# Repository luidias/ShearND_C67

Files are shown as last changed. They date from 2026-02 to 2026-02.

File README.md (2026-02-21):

# Noninjurious C6C7 Shear Data
This repository contains processed data used in the analysis of the biomechanical response of thirty-nine human Functional Spinal Units (FSUs) at the C6/C7 level when subjected to  pure shear loading. This data is provided here in full to facilitate FE model validation efforts. Detailed models of test fixturing is also included.

## Fixturing
This directory contains fixturing models and necessary information for their use.

- 'Assembly Diagrams.pdf' contains a labeled Bill of Materials and a schematic of how the components are assembled
- 'Fixturing Guide.pdf' contains information on fixture alignment as well as shear load and balancing mass application locations, and a more detailed Bill of Materials.

### Solidworks
This subdirectory contains models of all components (.SLDPRT) and the full assembly (.SLDASM) of the fixturing, generated in Solidworks 2025.

### STEP

This subdirectory contains models of all components as .STEP files, for wider compatibility with other CAD software. 
- The 'Individual Components' folder contains all component files separately.
- The 'Joined Components' folder contains aggregated .STEP files for the main fixturing and the mobile carriage. These must be positioned relative to each other according to the Disc Offset parameter. See the "Fixturing Guide" document for more details.

## Load-Displacement data

This directory contains sub-directories for each specimen (H1, H2, etc.), which in turn contain .csv files for individual tests on the given specimen. There are six files per specimen, one for each test condition (Anterior/posterior directions and 1, 10, and 100 mm/s). Test condition is reflected in the file name.

These files contain the 3D displacements, rotations, and loads that were experienced by the FSU under the respective test condition. The X, Y, and Z axes were aligned with the anatomical axes:
- X axis: Anteroposterior axis, with anterior as the positive direction. Shear loads were applied along this axis.
- Y axis: Craniocaudal (superior-inferior) axis. Cranial (superior) is positive.
- Z axis: Lateral axis. Right is positive.
  
Rotations around each axis follow the right hand rule: with the axis pointing out of the page, positive rotations are counter-clockwise.

The .csv files are laid out such that:
- Columns 1-3 are the X, Y, Z displacements of the superior vertebra relative to the inferior, measured im mm.
- Columns 4-6 are the X, Y, Z rotations of the same, measured in degrees.
- Columns 7-9 are the X, Y, Z loads generated during the test.
- Columns 10-12 are the X, Y, Z moments generated during the test, in Newton-Meters.

## Specimen Info.csv

This file contains demographic and anthropometric data for each specimen.
- **ID**: Identifier code for the specimen. Matches corresponding sub-directory in Load-displacement data directory.
- **Level**: FSU level. For this dataset, all specimens were at the C6/C7 level.
- **CT_Scanned**: Boolean representing whether CT scans were taken of the specimen.
- **ND_Test_Date**: Date when testing occured, in MM/DD/YYYY format.
- **Disc_Offset_mm**: The offset between the superior side of the fixturing and the load application point, adjusted for each specimen such that the loading line of action goes through the mid-disc plane, ensuring pure shear without any bending moment.
- **Specimen_Mass_kg**: Mass of the specimen, in kg, including PMMA potting, reinforcements, and specimen mounting plates
- **Balancing_Mass_kg**: Counterbalance mass used for the test, in kg, made up of half of the total specimen mass and the mass of the superior fixturing hardware.
- **Age**: Age of donor, in years.
- **Sex**: Biological sex of donor.
- **Race**: Race of donor.
- **Weight_kg**: Weight of donor at time of death, in kg.
- **Height_cm**: Height of donor at time of death, in cm.
- **Cause_of_death**: Donor cause of death.
- **sup_endplate_ap_width_from_lat_view_mm**: AP width of superior endplate proximal to the C6/C7 intervertebral disc, in mm. Measurements were taken from lateral X-ray images.
- **inf_endplate_ap_width_from_lat_view_mm**: Same as above, for the inferior endplate proximal to the disc.
- **avg_ap_width_from_lat_view_mm**: Average AP width of both proximal endplates.
- **avg_fsu_vertebral_body_volume_mm3**: averaged volume of the cancellous bone of both vertebral bodies, in mm<sup>3</sup>.
- **avg_vert_body_treb_bv_fraction**: Average bone volume fraction (BV/TV) of the cancellous bone in both vertebral bodies, as a ratio of bone volume to total volume.
- **Disc_Degen_Score**: Disc degeneration score, per the method established by Walraevens et al. [1], graded using CT scans. This is the sum of scores given to the disc for height loss, osteophytes, and endplate sclerosis. Possible scores are 0-9, where higher scores represent more degenerated discs.
- **Disc_Degen_Grade**: Disc degeneration grades correponding to the score. Possible values are None, Mild, Moderate, or Severe.
- **DD_Height_Loss**: Disc Height loss score. Possible scores of 0-4.
- **DD_Ant_OP**: Score for presence of anterior osteophytes, based on osteophyte size. Possible scores of 0-3.
- **DD_Endplate_Sclerosis**: Score for presence of proximal endplate sclerosis, based on severity. Possible scores of 0-2.
- **FJ_Degen_Score**: Facet Joint degeneration score, per Walraevens et al. [1], graded using CT scans. This is the sum of scores given for hypertrophy, osteophytes, articular irregularities, and joint space narrowing. Possible scores are 0-5, where higher scores represent more degenerated facet joints.
- **FJ_Degen_Grade**: Facet Joint degeneration grades correponding to the score. Possible values are None, Mild, Moderate, or Severe.
- **FJD_Hypertrophy**: Score for presence of hypertrophy. Possible scores are 0-2.
- **FJD_Osteophytes**: Score for presence of osteophytes. Possible scores are 0 or 1.
- **FJD_Surface_Irregularity**: Score for irregularity of articular surfaces. Possible scores are 0 or 1.
- **FJD_Joint_Narrowing**: Score for joint space narrowing. Possible scores are 0 or 1.

## Test Info.csv

This file contains information on specific tests carried out on the specimens. Each row entry represents one test. Specimen-specific data is repeated from Specimen Info.csv. Test-specific data is described below:
- **direction**: direction in which shear loads were applied (anterior or posterior).
- **disp_rate_mm_s**: displacement rate at which the test was carried out, in mm/s.
- **stiffness_1**: The Phase I Stiffness, in N/mm, calculated from the slope of the load-displacement data using a breakpoint analysis.
- **stiffness_2**: The Phase II Stiffness, in N/mm, calculated from the slope of the load-displacement data using a breakpoint analysis.
- **intercept_1**: Y-intercept of the linear regression from which Phase I stiffness was taken.
- **intercept_2**: Y-intercept of the linear regression from which Phase II stiffness was taken.
- **breakpoint_mm**: Location of breakpoint between the Phase I and Phase II response, on the displacement axis.
- **Calculated R2_1**: Goodness of fit (R<sup>2</sup>) for the Phase I regression line.
- **Calculated R2_2**: Goodness of fit (R<sup>2</sup>) for the Phase II regression line.
- **Calculated R2_3**: Goodness of fit (R<sup>2</sup>) for both regression lines in the breakpoint analysis.
- **peakLoad_N**: Maximum shear load during the test, in N.
- **peakDisp_mm**: maximum displacement during the test, in mm.

## References
[1] Walraevens J, Liu B, Meersschaert J, Demaerel P, Delye H, Depreitere B, et al. Qualitative and quantitative assessment of degeneration of cervical intervertebral discs and facet joints. Eur Spine J Off Publ Eur Spine Soc Eur Spinal Deform Soc Eur Sect Cerv Spine Res Soc. 2009 Mar;18(3):358–69

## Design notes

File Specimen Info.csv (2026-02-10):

ID | Level | CT_Scanned | ND_Test_Date | Disc_Offset_mm | Specimen_Mass_kg | Balancing_Mass_kg | Age | Sex | Race | Weight_kg | Height_cm | Cause_of_Death | sup_enplate_ap_width_from_lat_view_mm | inf_enplate_ap_width_from_lat_view_mm | avg_ap_width_from_lat_view_mm | avg_fsu_vertebral_body_volume_mm3 | avg_vert_body_treb_bv_fraction | Disc_Degen_Score | Disc_Degen_Grade | DD_Height_Loss | DD_Ant_OP | DD_Endplate_Sclerosis | FJ_Degen_Score | FJ_Degen_Grade | FJD_Hypertrophy | FJD_Osteophytes | FJD_Surface_Irregularity | FJD_Joint_Narrowing
H1 | C6C7 | TRUE | 7/8/2022 | 31.1 | 2.069 | 2.6535 | 67 | M | Caucasian | 120 | 180 | Myocardial Infarction | 15.4 | 14 | 14.7 | 1961.84 | 0.2045 | 1 | mild | 0 | 0 | 1 | 1 | mild | 0 | 0 | 0 | 1
H2 | C6C7 | TRUE | 6/29/2022 | 34.89 | 2.063 | 2.6505 | 73 | F |  |  |  |  | 16.5 | 15.7 | 16.1 | 1940.41 | 0.017 | 1 | mild | 0 | 1 | 0 | 1 | mild | 0 | 1 | 0 | 0
H3 | C6C7 | TRUE | 7/27/2022 | 28 | 2.04 | 2.639 | 69 | M |  |  |  |  | 17.3 | 16.8 | 17.05 | 2816.95 | 0.092 | 0 | none | 0 | 0 | 0 | 1 | mild | 0 | 1 | 0 | 0
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

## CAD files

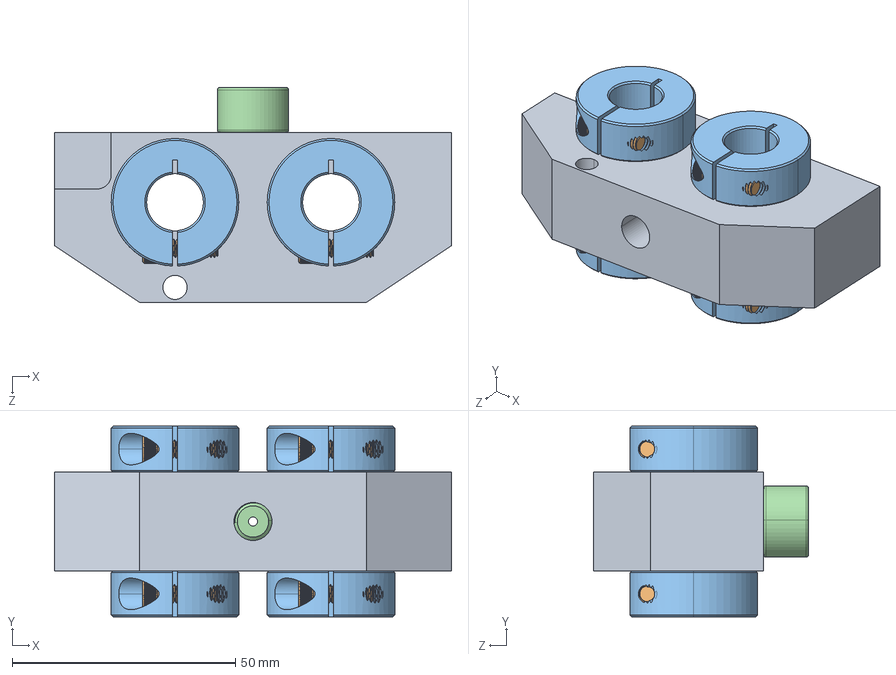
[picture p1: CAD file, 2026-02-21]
Fixturing/STEP/Joined Components/ND_Shear_Assembly_SinglePart_CarriageOnly.STEP
88.9 x 42.7 x 48.1 mm

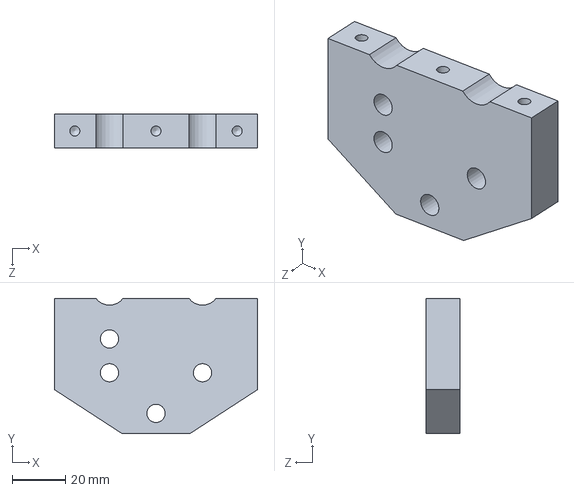
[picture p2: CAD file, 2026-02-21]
Fixturing/Solidworks/Outer gantry bracket, lower.SLDPRT
76.2 x 50.8 x 12.7 mm

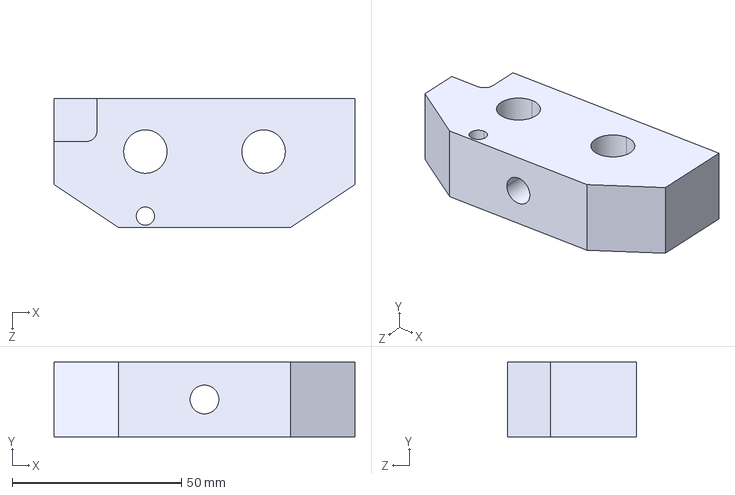
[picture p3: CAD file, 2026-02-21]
Fixturing/STEP/Individual components/Gantry Block.STEP
88.9 x 22.1 x 38.1 mm

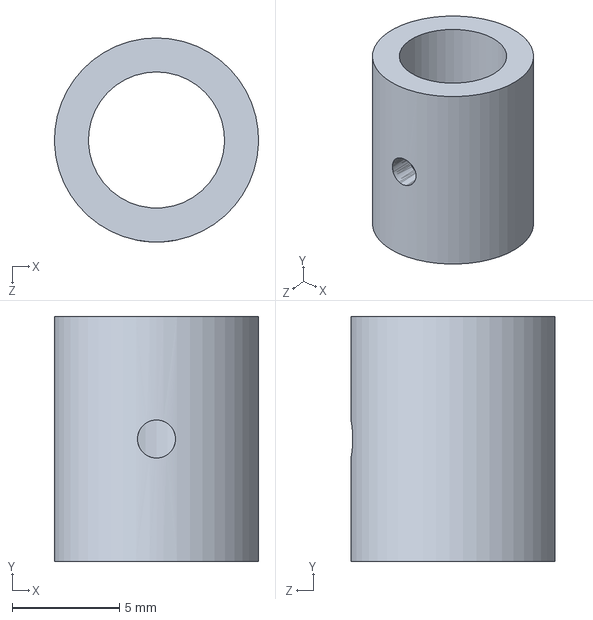
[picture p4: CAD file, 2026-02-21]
Fixturing/Solidworks/Spacer, small.SLDPRT
9.52 x 11.4 x 9.53 mm

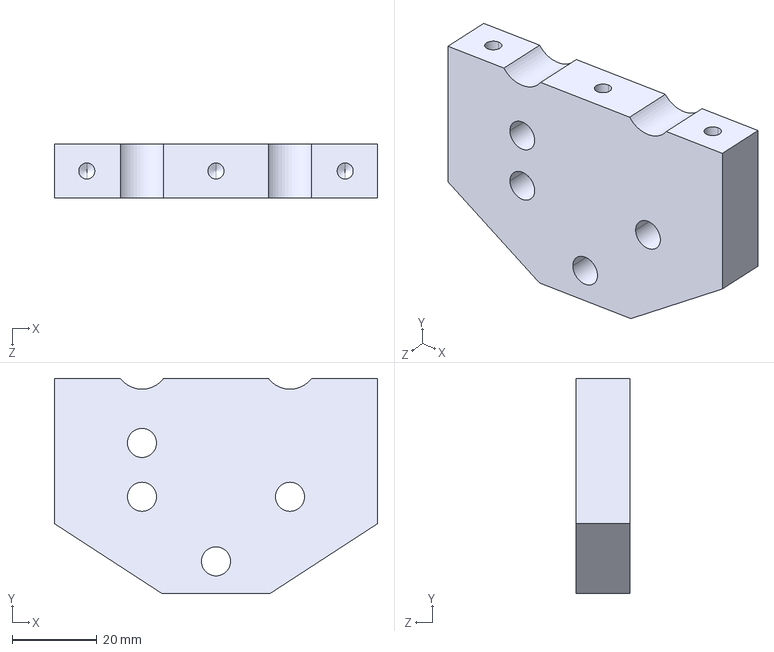
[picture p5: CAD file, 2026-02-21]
Fixturing/STEP/Individual components/Outer gantry bracket, lower.STEP
76.2 x 50.8 x 12.7 mm

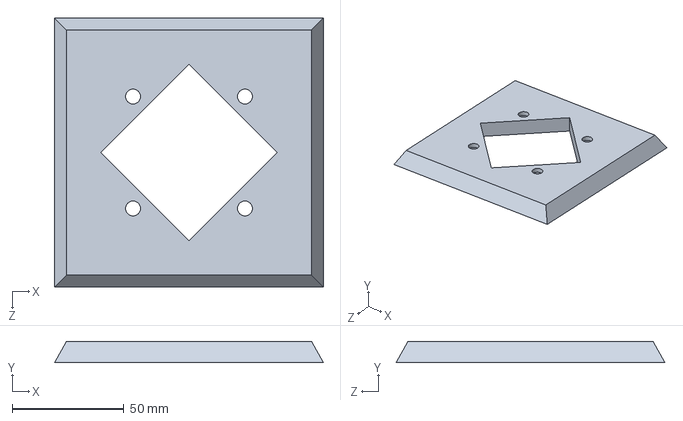
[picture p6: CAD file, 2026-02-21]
Fixturing/Solidworks/Specimen mounting plate.SLDPRT
120.2 x 9.53 x 120.2 mm

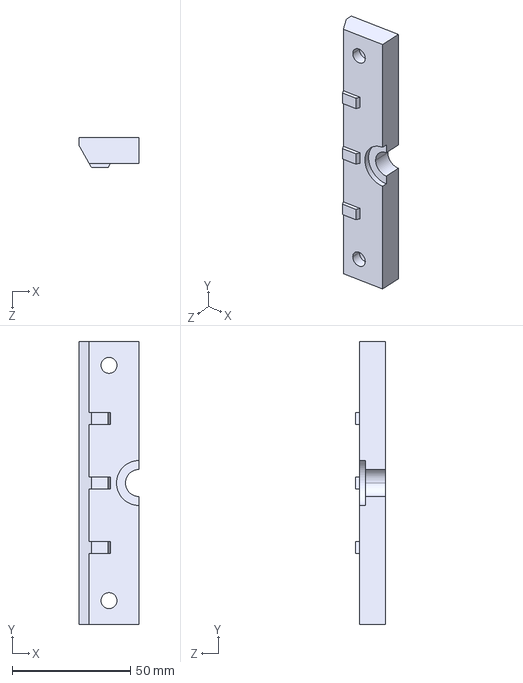
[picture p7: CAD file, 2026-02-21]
Fixturing/STEP/Individual components/Upper retainer.STEP
25.4 x 119.9 x 12.7 mm

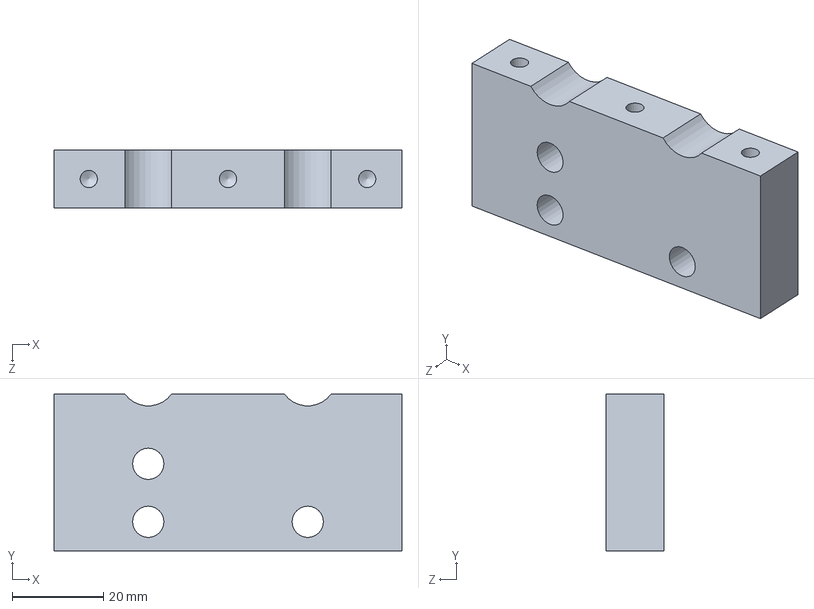
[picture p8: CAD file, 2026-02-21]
Fixturing/Solidworks/Inner gantry bracket, lower.SLDPRT
76.2 x 34.3 x 12.7 mm

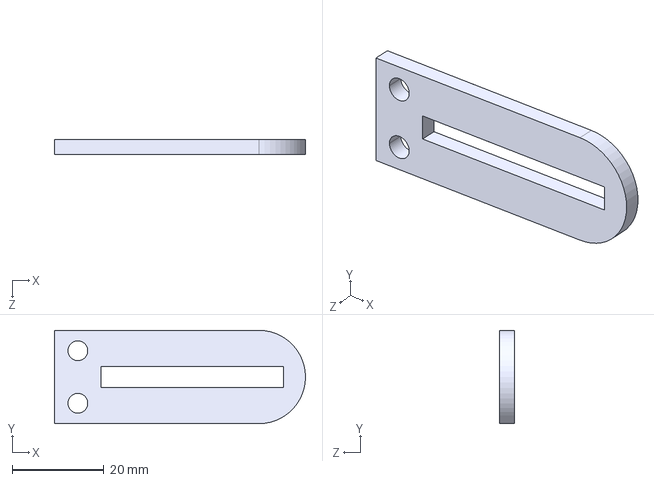
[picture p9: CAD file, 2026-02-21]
Fixturing/STEP/Individual components/Balancing bracket.STEP
54.6 x 20.3 x 3.17 mm

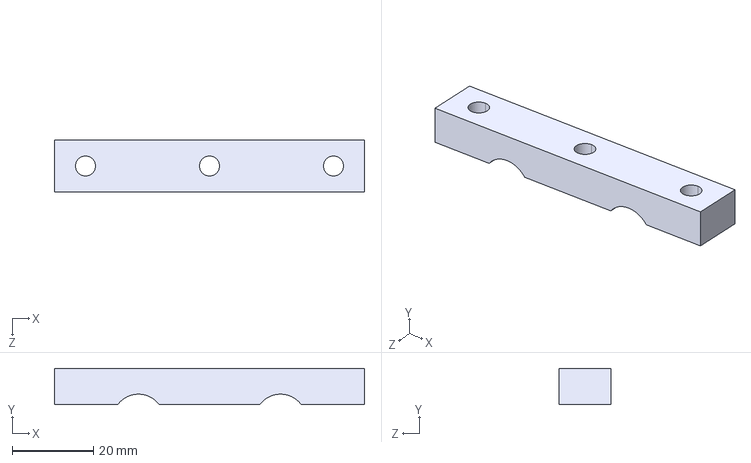
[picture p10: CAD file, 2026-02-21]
Fixturing/STEP/Individual components/Outer gantry bracket, upper.STEP
76.2 x 8.89 x 12.7 mm

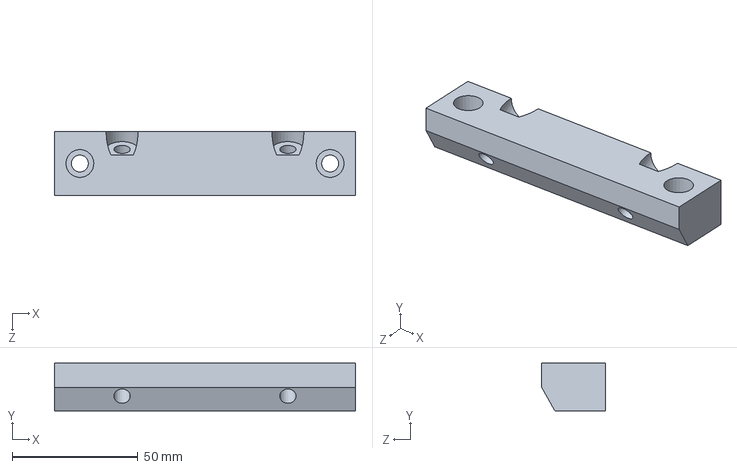
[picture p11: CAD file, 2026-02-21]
Fixturing/Solidworks/Lower retainer.SLDPRT
119.9 x 19.1 x 25.4 mm

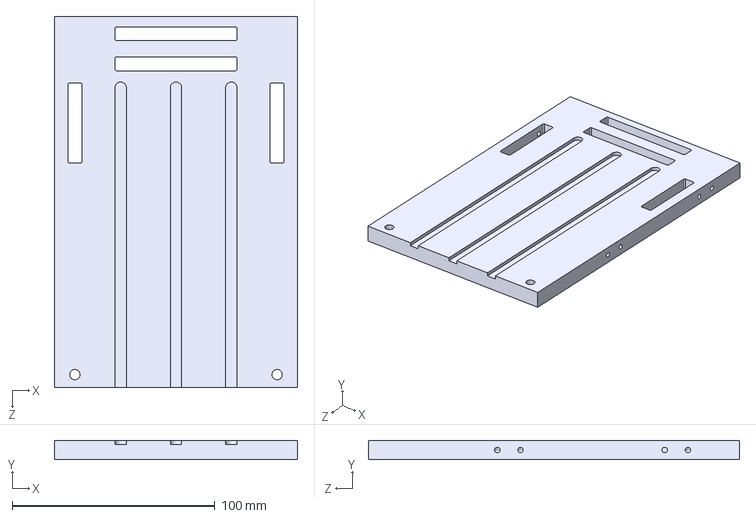
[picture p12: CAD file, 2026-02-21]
Fixturing/STEP/Individual components/Backing Plate.STEP
119.9 x 9.53 x 182.9 mm

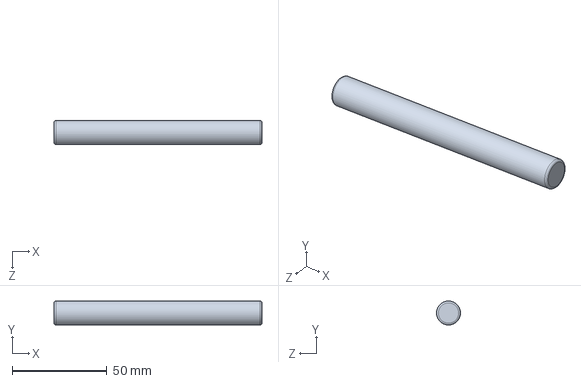
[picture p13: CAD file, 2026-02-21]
Fixturing/Solidworks/Gantry Rod.SLDPRT
110.0 x 12.7 x 12.7 mm

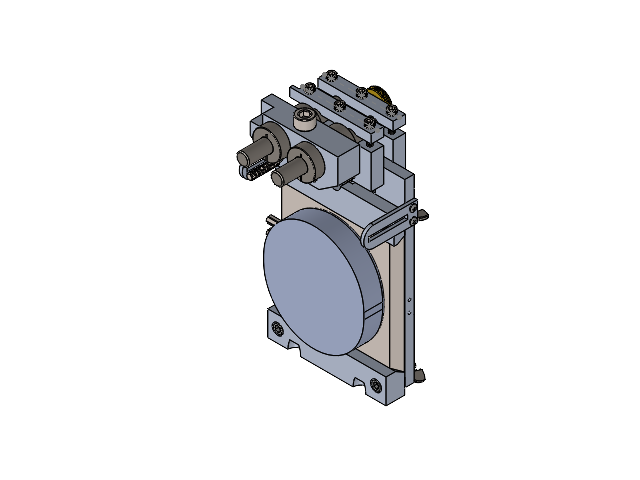
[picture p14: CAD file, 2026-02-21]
Fixturing/Solidworks/ND_Shear_Assembly.SLDASM
Backing Plate
5125K52_Brass Knob
Gantry Block
Gantry Rod x 2
Inner gantry bracket, lower
Inner gantry bracket, upper
Outer gantry bracket, lower
Outer gantry bracket, upper
Spacer, large
Spacer, small
92185A214_Super-Corrosion-Resistant 316 Stainless Steel Socket Head Screw x 6
90499A029_High-Strength Steel Hex Nut x 3
6435K34_Clamping Shaft Collar x 4
90126A206_Zinc-Plated Steel SAE Washer x 4
92580A332_Grade B7 Medium-Strength Steel Threaded Rod
92185A544_Super-Corrosion-Resistant 316 Stainless Steel Socket Head Screw
92185A548_Super-Corrosion-Resistant 316 Stainless Steel Socket Head Screw x 2
Lower retainer
Upper retainer
Specimen mounting plate
90866A029_Zinc-Plated Steel Wing Nut x 4
92196A540_18-8 Stainless Steel Socket Head Screw x 2
92196A544_18-8 Stainless Steel Socket Head Screw x 2
92311A581_18-8 Stainless Steel Cup-Point Set Screw x 2
91075A445_Male-Female Threaded Hex Standoff x 2
Balancing bracket x 2
91772A146_Passivated 18-8 Stainless Steel Pan Head Phillips Screw x 4
92196A537_18-8 Stainless Steel Socket Head Screw x 4
Cranial Potting
91292A046_18-8 Stainless Steel Socket Head Screw
92311A077_18-8 Stainless Steel Cup-Point Set Screw x 3

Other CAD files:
Fixturing/STEP/Individual components/ND_Shear_Assembly.STEP
Fixturing/Solidworks/Balancing bracket.SLDPRT
Fixturing/Solidworks/Gantry Block.SLDPRT
Fixturing/Solidworks/Outer gantry bracket, upper.SLDPRT
Fixturing/STEP/Individual components/5125K52_Brass Knob_5125K52.STEP
Fixturing/STEP/Individual components/6435K34_Clamping Shaft Collar_6435K34.STEP
Fixturing/STEP/Individual components/90126A206_Zinc-Plated Steel SAE Washer_90126A206.STEP
Fixturing/STEP/Individual components/90499A029_High-Strength Steel Hex Nut_90499A029.STEP
Fixturing/STEP/Individual components/90866A029_Zinc-Plated Steel Wing Nut_90866A029.STEP
Fixturing/STEP/Individual components/91075A445_Male-Female Threaded Hex Standoff_91075A445.STEP
Fixturing/STEP/Individual components/91292A046_18-8 Stainless Steel Socket Head Screw_91292A046.STEP
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

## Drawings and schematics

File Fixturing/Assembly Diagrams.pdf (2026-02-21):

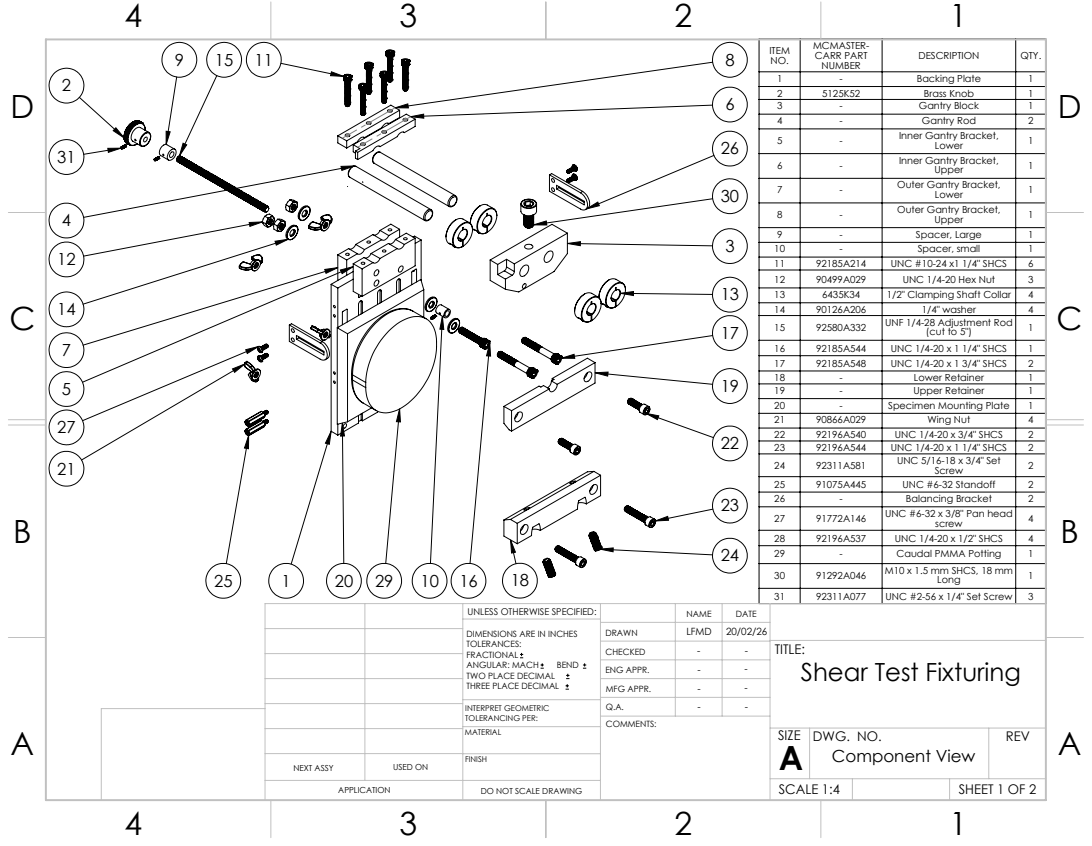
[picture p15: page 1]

ITEM NO. | MCMASTER-CARR PART NUMBER | DESCRIPTION | QTY.

1 | - Backing Plate | | 1
2 | 5125K52 | Brass Knob | 1
3 | - Gantry Block | | 1
4 | - Gantry Rod | | 2
5 | - Inner Gantry Bracket, | Lower | 1
6 | - Inner Gantry Bracket, | Upper | 1
7 | - Outer Gantry Bracket, | Lower | 1
8 | - Outer Gantry Bracket, | Upper | 1
9 | - Spacer, Large | | 1
10 | - Spacer, small | | 1
11 | 92185A214 | UNC #10-24 x1 1/4" SHCS | 6
12 | 90499A029 | UNC 1/4-20 Hex Nut | 3
13 | 6435K34 | 1/2" Clamping Shaft Collar | 4
14 | 90126A206 | 1/4" washer | 4
15 | 92580A332 | UNF 1/4-28 Adjustment Rod (cut to 5") | 1

16 | 92185A544 | UNC 1/4-20 x 1 1/4" SHCS | 1
17 | 92185A548 | UNC 1/4-20 x 1 3/4" SHCS | 2
18 | - Lower Retainer | | 1
19 | - Upper Retainer | | 1
20 | - Specimen Mounting Plate | | 1
21 | 90866A029 | Wing Nut | 4
22 | 92196A540 | UNC 1/4-20 x 3/4" SHCS | 2
23 | 92196A544 | UNC 1/4-20 x 1 1/4" SHCS | 2
24 | 92311A581 | UNC 5/16-18 x 3/4" Set Screw | 2
25 | 91075A445 | UNC #6-32 Standoff | 2
26 | - Balancing Bracket | | 2
27 | 91772A146 | UNC #6-32 x 3/8" Pan head screw | 4
28 | 92196A537 | UNC 1/4-20 x 1/2" SHCS | 4
29 | - Caudal PMMA Potting | | 1
30 | 91292A046 | M10 x 1.5 mm SHCS, 18 mm Long | 1

31 | 92311A077 | UNC #2-56 x 1/4" Set Screw | 3

UNLESS OTHERWISE SPECIFIED: | | NAME | DATE
DIMENSIONS ARE IN INCHES TOLERANCES: FRACTIONAL ANGULAR: MACH BEND TWO PLACE DECIMAL THREE PLACE DECIMAL | DRAWN | LFMD

CHECKED | | 20/02/26 --- | TITLE: Shear Test Fixturing
ENG APPR. | ---

MFG APPR.

INTERPRET GEOMETRIC TOLERANCING PER: | Q.A. | - | -
MATERIAL | | SIZE A | DWG. NO. Component View | REV

NEXT ASSY | USED ON | FINISH

APPLICATION | DO NOT SCALE DRAWING | | SCALE 1:4 | | SHEET 1 OF 2

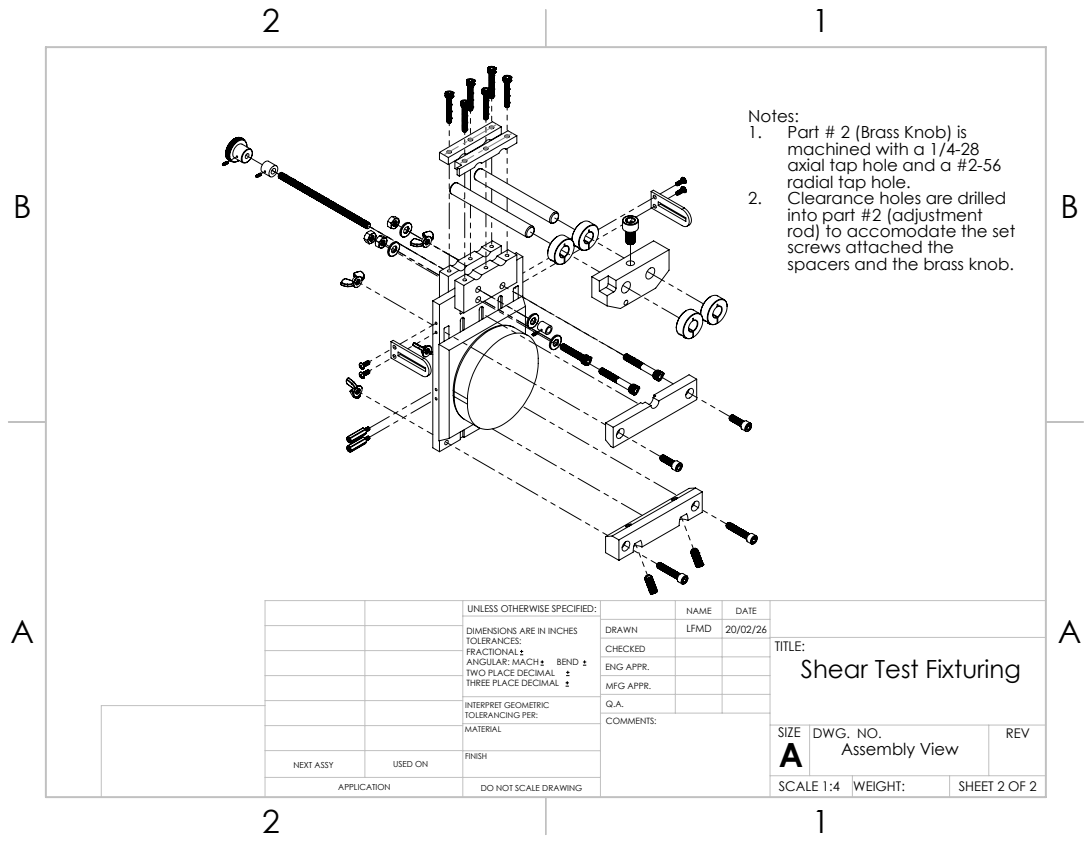
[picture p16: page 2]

Notes:
1. Part # 2 (Brass Knob) is
machined with a 1/4-28
axial tap hole and a #2-56
radial tap hole.
2. Clearance holes are drilled
into part #2 (adjustment
rod) to accomodate the set
screws attached the
spacers and the brass knob.

UNLESS OTHERWISE SPECIFIED: | | NAME | DATE
DIMENSIONS ARE IN INCHES TOLERANCES: FRACTIONAL ANGULAR: MACH BEND TWO PLACE DECIMAL THREE PLACE DECIMAL | DRAWN | LFMD | 20/02/26

CHECKED | | | TITLE: Shear Test Fixturing

ENG APPR.
MFG APPR.

INTERPRET GEOMETRIC TOLERANCING PER: | Q.A.
MATERIAL | | SIZE A | DWG. NO. Assembly View | REV

NEXT ASSY | USED ON | FINISH

APPLICATION | DO NOT SCALE DRAWING | | SCALE 1:4 | WEIGHT: | SHEET 2 OF 2

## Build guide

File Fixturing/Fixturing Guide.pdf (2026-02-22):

## Noninjurious C6C7 Shear Supplemental Data – Guide to fixturing

The following pages contain critical information on how the fixturing was set up and used in these experiments. A detailed Bill of Materials (BOM) is included, as well as a diagram of parts and assembly details. The repository includes models of all parts in Solidworks and .STEP file formats, to facilitate replication of the experiments using Finite Element Modeling (FEM)

Balancing Mass

The balancing mass, given by “Balancing_Mass_kg” in the “Test Info.csv” file, was a counterbalance applied to each specimen in order to counteract the effect of gravity and ensure the specimens started from a fully neutral position. The mass used for each test was equivalent to the mass of the fixturing plus one half of the mass of the potted specimen with mounting plates attached.

While in practice a series of pulleys was used, for FEM purposes this can be simplified by applying the equivalent force equally between the two balancing brackets (BOM Part #26) on either side of the fixture. The load application point is at the very end of the rectangular slot feature, as per the image below:

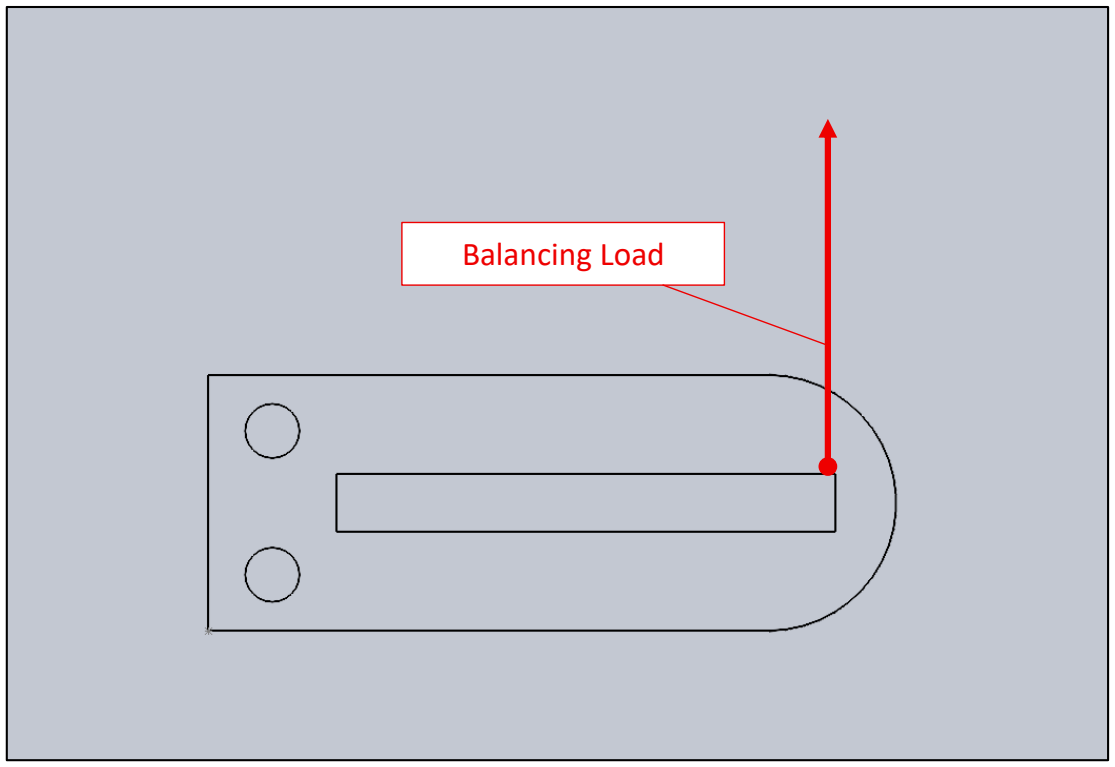
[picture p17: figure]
Balancing Load

Figure 1 - Balancing load location on balancing bracket. Each bracket support one half of the total balancing mass.

Important: Please take care to only apply half of the balancing force to each of the two balancing arms.

Shear Application Location

Shear was applied by displacing the M10x1.5 mm Screw (BOM Part # 30) upwards. This was done using a cable which was fed through the center hole drilled into the screw. Therefore, the displacement should be placed directly at the center of the top of this hole. Note that the cable cannot resist any other translations or any rotations, so the fixture must be translationally and rotationally unconstrained at this location aside from the displacement direction.

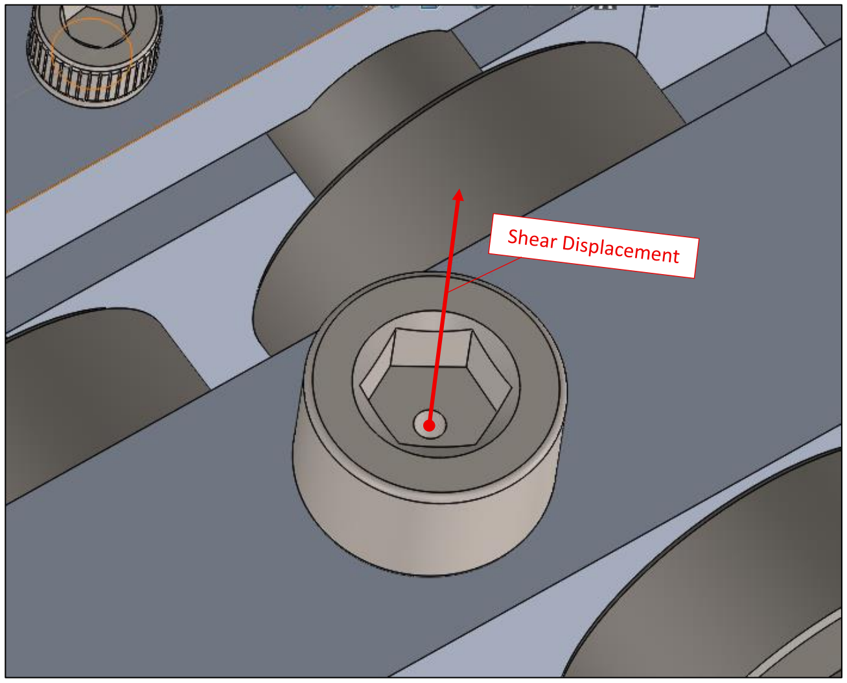
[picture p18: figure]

Figure 1 - Shear application location on carriage screw

Disc Offset

The disc offset (given by “Disc_Offset_mm” in the “Test Info.csv” file) is used to ensure that the shearing load is applied directly through the mid-disc plane, and that no combined bending moments are applied to the specimen.

The disc offset is measured along the craniocaudal axis from the bottom of the cranial potting to the centroid of the intervertebral disc. The Disc offset has been highlighted in the below cutout

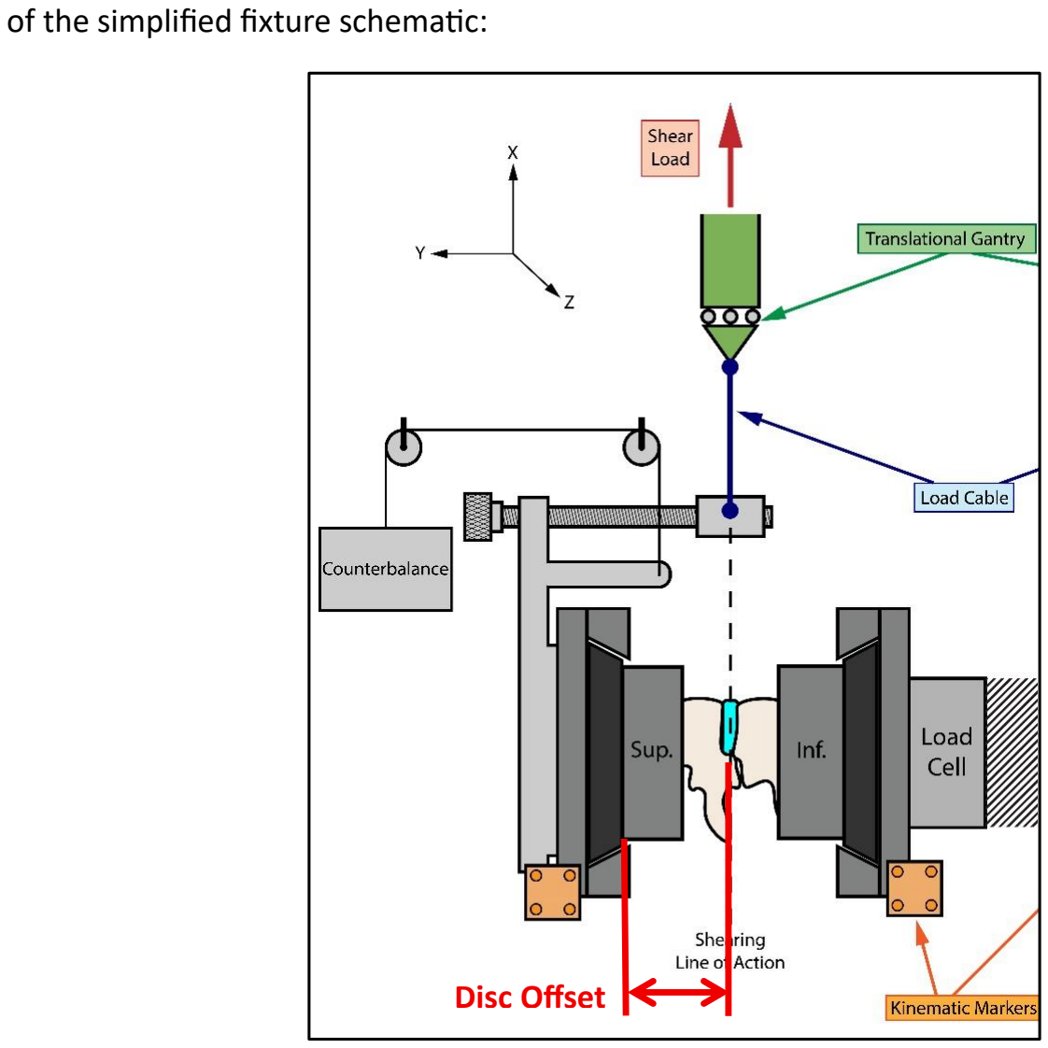
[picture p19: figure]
of the simplified fixture schematic:; Disc Offset

Figure 2 - Disc offset measurement on potted FSU in the shear loading fixture: between the bottom of the cranial/superior potting and the disc centroid.

The disc offset measurement should then be matched by the distance between the reference surfaces on the upper components of the fixture: namely, the distance (along the craniocaudal axis) between the reference surfaces on the Upper Inner Gantry Bracket (BOM Part #6) and the Gantry Block (BOM Part #3), as below:

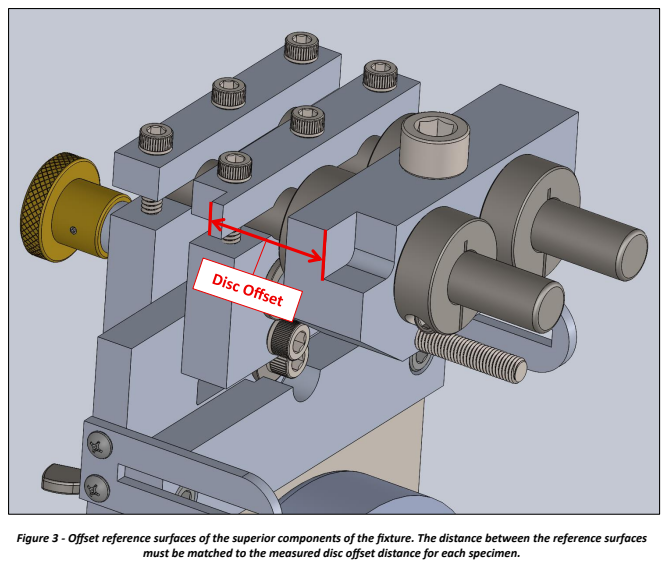
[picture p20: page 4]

Figure 3 - Offset reference surfaces of the superior components of the fixture. The distance between the reference surfaces

must be matched to the measured disc offset distance for each specimen.

A note on using these models in Finite Element Modeling (FEM) with Functional Spinal Units (FSUs):

Anatomical models of FSUs have not been included in this repository, and users must provide their own. When using a two-segment FSU model with this potting, the caudal FSU must be rigidly fixed in space, while the cranial FSU must be rigidly fixed to the cranial PMMA potting. The cranial vertebra can be attached to the potting at any depth so long as the intervertebral disc and facet joints are not occluded, and the loading line of action is appropriately aligned with the mid-disc plane using the Disc Offset measurement (see above). The specimen must be positioned with either the anterior or posterior direction facing up, depending on test orientation.

Care must be taken such that the intervertebral disc is coplanar with the shearing plane. This can be achieved using the average endplate angle as a landmark in the AP view, and the average angle of the anterior surfaces of the vertebral bodies as a landmark in the lateral view. A more detailed explanation of how this was achieved in our experiments can be found in the paper to which this repository belongs, in the methods sub-section titled “specimen preparation.”

Bill of Materials (BOM)

ITEM NO. | MCMASTER-CARR PART NUMBER | DESCRIPTION | QTY. | Material
1 | - | Backing Plate | 1 | 6061-T6 Aluminum
2 | 5125K52 | Brass Knob | 1 | Brass
3 | - | Gantry Block | 1 | 6061-T6 Aluminum
4 | - | Gantry Rod | 2 | Stainless Steel
5 | - | Inner Gantry Bracket, Lower | 1 | 6061-T6 Aluminum
6 | - | Inner Gantry Bracket, Upper | 1 | 6061-T6 Aluminum
7 | - | Outer Gantry Bracket, Lower | 1 | 6061-T6 Aluminum
8 | - | Outer Gantry Bracket, Upper | 1 | 6061-T6 Aluminum
9 | - | Spacer, Large | 1 | 6061-T6 Aluminum
10 | - | Spacer, small | 1 | 6061-T6 Aluminum
11 | 92185A214 | UNC #10-24 x1 1/4" SHCS | 6 | Stainless Steel
12 | 90499A029 | UNC 1/4-20 Hex Nut | 3 | Steel
13 | 6435K34 | 1/2" Clamping Shaft Collar | 4 | Stainless Steel
14 | 90126A206 | 1/4" washer | 4 | Steel
15 | 92580A332 | UNF 1/4-28 Adjustment Rod (cut to 5") | 1 | Steel
16 | 92185A544 | UNC 1/4-20 x 1 1/4" SHCS | 1 | Stainless Steel
17 | 92185A548 | UNC 1/4-20 x 1 3/4" SHCS | 2 | Stainless Steel
18 | - | Lower Retainer | 1 | 6061-T6 Aluminum
19 | - | Upper Retainer | 1 | 6061-T6 Aluminum
20 | - | Specimen Mounting Plate | 1 | Stainless Steel
21 | 90866A029 | Wing Nut | 4 | Steel
22 | 92196A540 | UNC 1/4-20 x 3/4" SHCS | 2 | Stainless Steel
23 | 92196A544 | UNC 1/4-20 x 1 1/4" SHCS | 2 | Stainless Steel
24 | 92311A581 | UNC 5/16-18 x 3/4" Set Screw | 2 | Stainless Steel
25 | 91075A445 | UNC #6-32 Standoff | 2 | Stainless Steel
26 | - | Balancing Bracket | 2 | 6061-T6 Aluminum
27 | 91772A146 | UNC #6-32 x 3/8" Pan head screw | 4 | 6061-T6 Aluminum
28 | 92196A537 | UNC 1/4-20 x 1/2" SHCS | 4 | 6061-T6 Aluminum
29 | - | Cranial PMMA Potting | 1 | Bosworth Fastray Bone Cement
30 | 91292A046 | M10 x 1.5 mm SHCS, 18 mm Long | 1 | Stainless Steel
31 | 92311A077 | UNC #2-56 x 1/4" Set Screw | 3 | Stainless Steel

Notes:

- Components with no part numbers were manufactured in-house and are not available as off-the-shelf parts.
- All components with a part number were purchased from McMaster-Carr (https://www.mcmaster.com/).
- After purchase, component #2 was further modified with two tap holes and component # 15 was trimmed to size. Details on these modifications can be found in the model files.

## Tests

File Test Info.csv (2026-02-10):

ID | level | direction | disp_rate_mm_s | stiffness_1 | stiffness_2 | intercept_1 | intercept_2 | breakpoint_mm | calculated_R2_1 | calculated_R2_2 | calculated_R2_3 | peakLoad_N | peakDisp_mm | CT_Scanned | Disc_Offset_mm | Specimen_Mass_kg | Balancing_Mass_kg | Age | Sex | Race | Weight_kg | Height_cm | Cause_of_Death | sup_enplate_ap_width_from_lat_view_mm | inf_enplate_ap_width_from_lat_view_mm | avg_ap_width_from_lat_view_mm | avg_fsu_vertebral_body_volume_mm3 | avg_vert_body_treb_bv_fraction | Disc_Degen_Score | Disc_Degen_Grade | DD_Height_Loss | DD_Ant_OP | DD_Endplate_Sclerosis | FJ_Degen_Score | FJ_Degen_Grade | FJD_Hypertrophy | FJD_Osteophytes | FJD_Surface_Irregularity | FJD_Joint_Narrowing
H1 | C67 | Ant | 1 | 225.42752 | 257.0098328 | -5.903334593 | -19.82641754 | 0.440850644 | 0.997979576 | 0.99836642 | 0.999583359 | 218.2467318 | 0.925093678 | TRUE | 31.1 | 2.069 | 2.6535 | 67 | M | Caucasian | 120 | 180 | Myocardial Infarction | 15.4 | 14 | 14.7 | 1961.84 | 0.2045 | 1 | mild | 0 | 0 | 1 | 1 | mild | 0 | 0 | 0 | 1
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

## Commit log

2025-12-10 Update and rename H1_C67_Ant_100_mm_s.csv to H1_C67_Ant_100_mm_s.csv
    Rename directories for better sort order
    [H1_C67_Ant_100_mm_s.csv]
2026-02-10 add further details
    [H10_C67_Ant_100_mm_s.csv, H10_C67_Ant_10_mm_s.csv, H10_C67_Ant_1_mm_s.csv, H10_C67_Pos_100_mm_s.csv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]
2026-02-21 Add fixturing models and associated files
    [5125K52_Brass Knob.SLDPRT, 5125K52_Brass Knob_5125K52.STEP, 6435K34_Clamping Shaft Collar.SLDPRT, 6435K34_Clamping Shaft Collar_6435K34.STEP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]
